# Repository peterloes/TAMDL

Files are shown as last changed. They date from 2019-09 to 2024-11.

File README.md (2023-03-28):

# Timed Animal Manipulation Data Logger (TAMDL)
### use timers to trigger your devices

Authors: Loës P., Kempenaers B. (2019) 

Platform for animal observation and manipulation. 

An efficient system to monitor animal behaviour in wildlife
as well as in laboratory settings.

-	Compatible with different RFID systems and triggers
-	Low power consumption and specific data collection lead to long lasting collection periods
-	Applicable world-wide due to its compatibility with different types of radio clock receivers 
-	High observation quality through low disturbance of the animals
- Three user-defined power outputs that can individually be switched on or off at user-defined times

My image

- Time Synchronization with atomic clock once a day to ensure optimal data quality
- Current Control twice a day
- Forecast for Battery-Change implemented
- Energy Bypass so that Date and Time are maintained even when changing battery
- Hyperterminal Output, to get real-time data to the computer/laptop
- Low-Power Device 
- Measure Voltage and Current from your triggered devices 
 
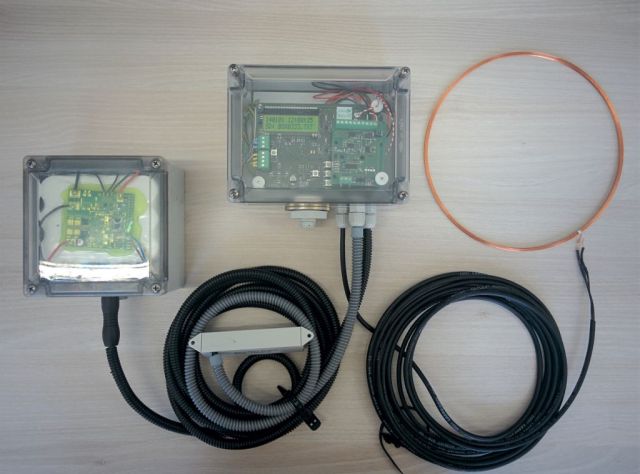
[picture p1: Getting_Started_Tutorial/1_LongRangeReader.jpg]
My image


Picture: Prototype "Activity Logger" with RFID-Reader

https://github.com/peterloes/TAMDL/blob/master/Getting_Started_Tutorial/1_poster_overview_2.pdf

Timed camera trap on nestbox top:

https://github.com/peterloes/TAMDL/blob/master/Getting_Started_Tutorial/1_poster_overview_1.pdf

Raw data on SD Card:

https://github.com/peterloes/TAMDL/blob/master/Getting_Started_Tutorial/6_rawdata_BOX0999.TXT

Configuration data on SD Card:

https://github.com/peterloes/TAMDL/blob/master/Software/CONFIG.TXT

Optional components:

https://github.com/peterloes/Light_Barrier

https://github.com/peterloes/Servo_Engine

https://github.com/peterloes/Linear_Engine

https://github.com/peterloes/Booter_RFID-MS_MOMO_TAMDL

https://github.com/peterloes/Clock_receiver_RFID-MS_MOMO_TAMDL

Manufacture:

https://github.com/peterloes/TAMDL/blob/master/Getting_Started_Tutorial/5_Supplier.txt

C is the Greenest Programming Language

To achieve its power and energy-efficiency features, EFM32 products utilize ultralow active and idle power,
fast wakeup and processing times, and most important, the ability to intelligently interact with peripherals
and sensors autonomously without waking up the CPU and consuming more power.

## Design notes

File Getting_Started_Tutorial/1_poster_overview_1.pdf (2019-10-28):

### Timed Animal Manipulation Data Logger (TAMDL)

### Automating the recording and manipulation of animal behavior

Peter Loës & Peter Skripsky Department Kempenærs

Uses of TAMDL:

- Timed activation of devices such as solar panels, automatic feeders, animal traps, and other electronic devices
- Ideal for nest boxes, roosting boxes, and open nests
- Can be combined with many external triggers such as pit tag (RFID) readers, camera traps, light barriers, lights, etc.
- Manipulation of organisms at e.g. simulating early light/dawn with timed lights in nest boxes

8,3 mm

RFID tag/transponder

Timed camera
trap on top

Timed RFID
reader in nest
box (records ID)

Example use of TAMDL (e.g. nest box):

Benefits of TAMDL:

- Automated device → no observer bias, accurate recording, minimal disturbance to study species
- Only uses sleep and deep sleep mode to save battery life
- Large SD card data storage
- Timer connected to external devices (e.g. camera trap) lets you control the amount of data collected and energy output

LCD can be used to view
settings (pushbuttons on
the circuit board to go
through different settings)

Example Timer Setup:

Operating times for UA1 output [hour:min] → Camera Trap
UA1_ON_TIME_1 | = 23:00
UA1_OFF_TIME_1 | = 00:00
UA1_ON_TIME_2 | = 05:00
UA1_OFF_TIME_2 | = 06:00
UA1_ON_TIME_3 | = 11:00
UA1_OFF_TIME_3 | = 12:00
UA1_ON_TIME_4 | = 17:00
UA1_OFF_TIME_4 | = 18:00
Operating times for UA2 output [hour:min] → RFID Reader
UA2_ON_TIME_1 | = 09:00
UA2_OFF_TIME_1 | = 11:00

Max-Planck-Institut
für Ornithologie

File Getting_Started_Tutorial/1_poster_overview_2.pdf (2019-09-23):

### Timed Animal Manipulation Data Logger (TAMDL)

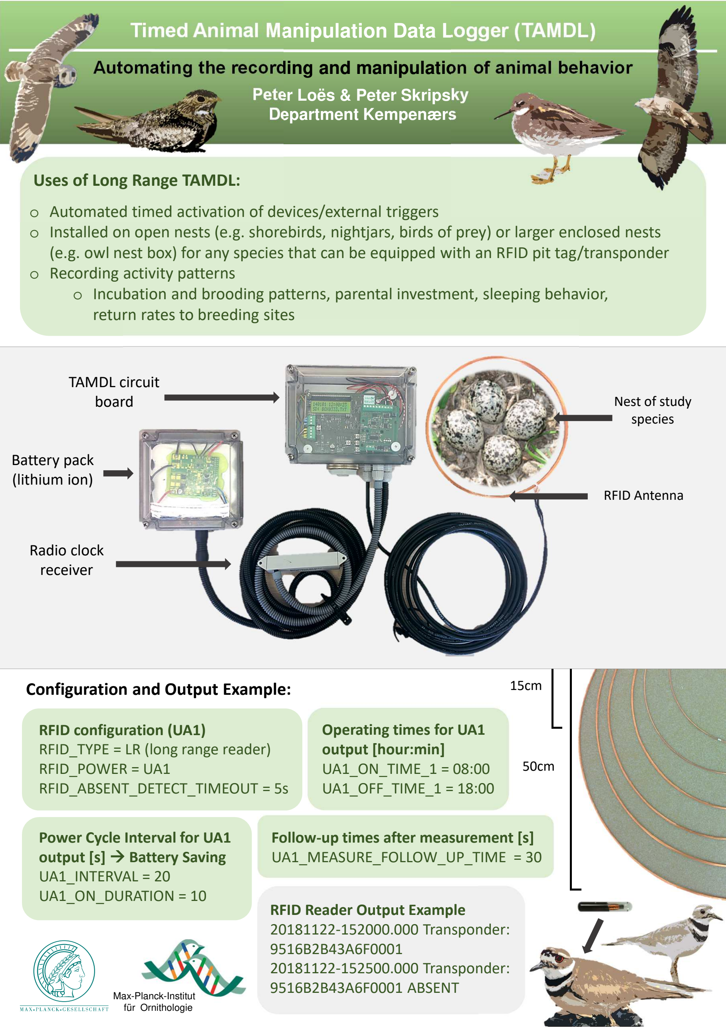
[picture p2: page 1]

Automating the recording and manipulation of animal behavior

Peter Loës & Peter Skripsky Department Kempenærs

TAMDL circuit
board

Battery pack
(lithium ion)

Radio clock
receiver

RFID Antenna

Nest of study
species

Uses of Long Range TAMDL:

- Automated timed activation of devices/external triggers
- Installed on open nests (e.g. shorebirds, nightjars, birds of prey) or larger enclosed nests (e.g. owl nest box) for any species that can be equipped with an RFID pit tag/transponder
- Recording activity patterns
- Incubation and brooding patterns, parental investment, sleeping behavior,
return rates to breeding sites

Configuration and Output Example:

50cm

15cm

Operating times for UA1
output [hour:min]
UA1_ON_TIME_1 = 08:00
UA1_OFF_TIME_1 = 18:00

Power Cycle Interval for UA1 output [s] → Battery Saving UA1_INTERVAL = 20
UA1_ON_DURATION = 10

RFID configuration (UA1)
RFID_TYPE = LR (long range reader) RFID_POWER = UA1
RFID_ABSENT_DETECT_TIMEOUT = 5s

RFID Reader Output Example 20181122-152000.000 Transponder: 9516B2B43A6F0001
20181122-152500.000 Transponder: 9516B2B43A6F0001 ABSENT Max-Planck-Institut

für Ornithologie

Follow-up times after measurement [s] UA1_MEASURE_FOLLOW_UP_TIME = 30

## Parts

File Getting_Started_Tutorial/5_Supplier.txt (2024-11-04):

Active antennas
DCF77 Empfänger AASV DCFn PON/Ri/1m Aktivantenne SV DCFn 

HKW-Elektronik GmbH
Jörg Schneider

Eisenacher Str. 42 b
99848 Wutha-Farnroda / Thür.
Germany
Phone:  +49 (0)36921 3080 130
mailto:    schneider@hkw-elektronik.de
www.hkw-elektronik.de

Lithium Ionen rechargeable battery pack Art.Nr. 60.16294 Panasonic NCR 18650GA 4S2P
14,4Volt 6900mAh inklusive SMBus Kabel je. 150mm 

DYNAMIS Batterien GmbH
Josef Pfeil

Brühlstraße 15  D- 78465 Dettingen / Konstanz
Tel. +49 (0) 75 33/93 669-15
mailto:josef.pfeil@dynamis-batterien.de
www.dynamis-batterien.de

RFID Reader Lichtschranke Artikenr.:170201-00/0 (Long Range)
//Input power supply max. 15Volt

AFRO Fluginstrumente GmbH
Andreas Frommwieser

Bahnhofstr. 37
D - 83253 Rimsting / Chiemsee
Tel.: +49 (0)8051 / 61249
Mobil:+49 (0)151/22 684 697
www.AFRO-Fluginstrumente.de
A.Frommwieser@AFRO-Fluginstrumente.de

MOUSER ELECTRONICS

Texas Instruments 12-mm low-frequency (LF) glass transponders
Frequency of 134.2 kHz
Artikelnr.: 595-TRPGR30ATGC

Supplier of all Electronic Boards

Top-Print Electronic GmbH
Oskar Schmid

Rosenheimer Landstr. 129a
85521 Ottobrunn
Germany
Tel.: +49-89-60668047
Fax: +49-89-60668049
mailto: info@top-print.eu
https://www.leiterplatten-muenchen.de/

RFID reader
Nanomodule Multi 125LV A/1.11 (T3NM-LV) 125kHz +/-0,5% Art.Nr. ART10413
ANT002 Rundspule 47mm, 490µH Art.Nr. ART 10668

Elatec GmbH
Felix Ellspermann

Zeppelinstr. 1
82178 Puchheim 
Germany
Tel: +49 89 552 9961 120
mailto: f.ellspermann@elatec.com
www.elatec-rfid.com

Small sized transponder, not uniqued.
GlassTag 1,41x8,3mm EM4305 134kHz

Programming required for transponders.

Rasmus Forntheil
Product Manager Animal ID
RBIS Europe, Smartrac Specialty GmbH

e: rasmus.forntheil@eu.averydennison.com
t: +49 (0) 2265 9919-14  |  m: +49 (0) 173 5688184
Gewerbeparkstr. 10, 51580 Reichshof-Wehnrath, Germany

Internet: https://www.averydennison.com/en/home.html

Protective coating with Schmelzharz Bectron MR3404

KC – Kunststoff- Chemische Produkte GmbH
Holger Sarau-Burghardt

Leonberger Straße 86 
DE 71292 Friolzheim
phone: +49 (0)7044 9425 13
e-mail: h.sarau-burghardt@kc-produkte.com
http: www.conformalcoating.de

Industrial SD Cards ATP 2GB
https://www.atpinc.com/products/industrial-sd-cards

FTDI Chip cable (3.5mm Audio Jack to USB)
TTL-232R-3V3-AJ

Housing
https://www.spelsberg.de/industrieleergehaeuse/glatt-mit-befestigungsnocken/20100701/
TG PC 1612-9-to
Artikelnummer: 20100701 | Maße: 162 x 122 x 90 mm
Leergehäuse IP66 / IP67 Polycarbonat

iTracker DashCam Mini0801
Please contact me to get the electronic board for IR_Light_DashCam. (Hardware_EagleFiles)

Docklight RS232 Terminal / RS232 Monitor
https://docklight.de/information/

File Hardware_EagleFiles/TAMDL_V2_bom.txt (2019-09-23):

Part  Value                                             Device                  Package                Description                                                    MPN     OC_FARNELL OC_NEWARK PACKAGE  SUPPLIER         
C1    100µF/25V                                         CPOL-EUE                PANASONIC_E            POLARIZED CAPACITOR, European symbol                                                                                  
C2    10µF/25V                                          C-EUC1206               C1206                  CAPACITOR, European symbol                                                                                            
C3    22µF/10V                                          C-EUC0603               C0603                  CAPACITOR, European symbol                                                                                            
C4    EECS0HD 224;Panasonic                             GOLDCAPSPK-V            GOLDCAPSPK-V                                                                                                                                 
C5    100µF/25V                                         CPOL-EUE                PANASONIC_E            POLARIZED CAPACITOR, European symbol                                                                                  
C6    100µF/25V                                         CPOL-EUE                PANASONIC_E            POLARIZED CAPACITOR, European symbol                                                                                  
C7    100nF/16V                                         C-EUC0805               C0805                  CAPACITOR, European symbol                                                                                            
C8    100nF/16V                                         C-EUC0805               C0805                  CAPACITOR, European symbol                                                                                            
C9    10µ/25V                                           C-EUC1206               C1206                  CAPACITOR, European symbol                                                                                            
C10   100n                                              C_SMD0805               0805                                                                                                                                         
C11   1u                                                C_SMD0805               0805                                                                                                                                         
C12   18p                                               C_SMD0805               0805                                                                                                                                         
C13   12p                                               C_SMD0805               0805                                                                                                                                         
C14   100n                                              C_SMD0805               0805                                                                                                                                         
C15   100n                                              C_SMD0805               0805                                                                                                                                         
C16   100n                                              C_SMD0805               0805                                                                                                                                         
C17   18p                                               C_SMD0805               0805                                                                                                                                         
C18   12p                                               C_SMD0805               0805                                                                                                                                         
C19   10µ                                               C_SMD0805               0805                                                                                                                                         
C20   100n                                              C_SMD0805               0805                                                                                                                                         
C21   100n                                              C_SMD0805               0805                                                                                                                                         
C22   100n                                              C_SMD0805               0805                                                                                                                                         
C23   100n                                              C_SMD0805               0805                                                                                                                                         
C24   100n                                              C_SMD0805               0805                                                                                                                                         
C25   10µ                                               C_SMD0805               0805                                                                                                                                         
C26   10nF                                              C-EUC0603               C0603                  CAPACITOR, European symbol                                                                                            
C27   10nF                                              C-EUC0603               C0603                  CAPACITOR, European symbol                                                                                            
C28   10nF                                              C-EUC0603               C0603                  CAPACITOR, European symbol                                                                                            
C29   10nF                                              C-EUC0603               C0603                  CAPACITOR, European symbol                                                                                            
C30   10nF                                              C-EUC0603               C0603                  CAPACITOR, European symbol                                                                                            
C31   10n                                               C-EUC0603               C0603                  CAPACITOR, European symbol                                                                                            
C32   100nF                                             C-EUC0603               C0603                  CAPACITOR, European symbol                                                                                            
C33   100nF                                             C-EUC0603               C0603                  CAPACITOR, European symbol                                                                                            
C34   4.7µF                                             C-EUC1210               C1210                  CAPACITOR, European symbol                                                                                            
C35   4.7µF                                             C-EUC1210               C1210                  CAPACITOR, European symbol                                                                                            
C36   n.b.                                              C-EUC1210               C1210                  CAPACITOR, European symbol                                                                                            
C37   n.b.                                              C-EUC1210               C1210                  CAPACITOR, European symbol                                                                                            
C38   10nF                                              C-EUC0603               C0603                  CAPACITOR, European symbol                                                                                            
C39   10nF                                              C-EUC0603               C0603                  CAPACITOR, European symbol                                                                                            
C40   100nF                                             C-EUC0603               C0603                  CAPACITOR, European symbol                                                                                            
C41   100nF                                             C-EUC0603               C0603                  CAPACITOR, European symbol                                                                                            
C42    n.b.                                             C-EUC0603               C0603                  CAPACITOR, European symbol                                                                                            
C43    n.b.                                             C-EUC0603               C0603                  CAPACITOR, European symbol                                                                                            
C44   4.3nF                                             C-EUC0603               C0603                  CAPACITOR, European symbol                                                                                            
C45   4.3nF                                             C-EUC0603               C0603                  CAPACITOR, European symbol                                                                                            
C46   24pF                                              C-EUC0603               C0603                  CAPACITOR, European symbol                                                                                            
C47   24pF                                              C-EUC0603               C0603                  CAPACITOR, European symbol                                                                                            
C48    n.b.                                             C-EUC0603               C0603                  CAPACITOR, European symbol                                                                                            
C49    n.b                                              C-EUC0603               C0603                  CAPACITOR, European symbol                                                                                            
C50   22µF                                              C-EUC1210               C1210                  CAPACITOR, European symbol                                                                                            
C51   22µF                                              C-EUC1210               C1210                  CAPACITOR, European symbol                                                                                            
C52   22µF                                              C-EUC1210               C1210                  CAPACITOR, European symbol                                                                                            
C53   22µF                                              C-EUC1210               C1210                  CAPACITOR, European symbol                                                                                            
C54   n.b.                                              C-EUC1210               C1210                  CAPACITOR, European symbol                                                                                            
C55   n.b.                                              C-EUC1210               C1210                  CAPACITOR, European symbol                                                                                            
C56   10µF                                              C-EUC1206               C1206                  CAPACITOR, European symbol                                                                                            
C57   10µF                                              C-EUC1206               C1206                  CAPACITOR, European symbol                                                                                            
C58   100nF                                             C-EUC0603               C0603                  CAPACITOR, European symbol                                                                                            
C59   100nF                                             C-EUC0603               C0603                  CAPACITOR, European symbol                                                                                            
C60   100nF                                             C-EUC0603               C0603                  CAPACITOR, European symbol                                                                                            
C61   1nF                                               C-EUC0603               C0603                  CAPACITOR, European symbol                                                                                            
C62   1nF                                               C-EUC0603               C0603                  CAPACITOR, European symbol                                                                                            
C63   100nF                                             C-EUC0603               C0603                  CAPACITOR, European symbol                                                                                            
C64   470n                                              C-EUC0805               C0805                  CAPACITOR, European symbol                                                                                            
C65   100n                                              C-EUC1206               C1206                  CAPACITOR, European symbol                                                                                            
D1    BAT54C                                            D2A_SOT23               SOT-23$1               Dual DIODE                                                                                                            
D2    BAT54C                                            D2A_SOT23               SOT-23$1               Dual DIODE                                                                                                            
D3    BAT54C                                            D2A_SOT23               SOT-23$1               Dual DIODE                                                                                                            
D4    B360B                                             SCHOTTKY-DIODESMD       SMB                    Schottky Diode                                                                                                        
D5    B360B                                             SCHOTTKY-DIODESMD       SMB                    Schottky Diode                                                                                                        
D6    MBR2H200SFT1G                                     SMF5.0AT1               SOD123FL               200 W Transient Voltage Suppressor                                                                                    
D7    MBR2H200SFT1G                                     SMF5.0AT1               SOD123FL               200 W Transient Voltage Suppressor                                                                                    
F1    MF-USMF110                                        PFUF                    PFUF_1210POLY                                                                                                                                
F2    MF-USMF110                                        PFUF                    PFUF_1210POLY                                                                                                                                
F3    MF-USMF110                                        PFUF                    PFUF_1210POLY                                                                                                                                
F4    MF-USMF150                                        PFUF                    PFUF_1210POLY                                                                                                                                
F5    MF-USMF150                                        PFUF                    PFUF_1210POLY                                                                                                                                
IC1   TPS62125                                          TPS62125                DSG_PWSO-N8_EXP                                                                                                                              
IC2   EFM32G230F128                                     EFM32G230F128           QFN64                  EFM32G230F128 Gecko Microcontroller in 9mm x 9mm QFN64 package                                                        
IC3   TPS54240DGQR                                      TPS54240DGQR            S-PDSO-G10                                                                                                                                   
IC4   TPS54240DGQR                                      TPS54240DGQR            S-PDSO-G10                                                                                                                                   
IC5   LTC6102IDD-1                                      LTC6102IDD-1            DFN8-LEAD                                                                                                                                    
IC6   LTC6102IDD-1                                      LTC6102IDD-1            DFN8-LEAD                                                                                                                                    
J1    LUMBERG1502_01                                    LUMBERG1502_01          LUMBERG1502_01                                                                                                                               
L1    LPS3008/22µH                                      LPS3008                 LPS3008                                                                                                                                      
L2    BLM21B102S                                        WE-CBF-7427920_0805     0805                   SMD EMI Suppression Ferrite Beads WE-CBF                       7427920 1635707    08P2358   IND-0805 Wuerth Elektronik
L3    PIS4728                                           DR127                   DR127                  High Power Density, High Efficiency, Shielded Inductors                                                               
L4    PIS4728                                           DR127                   DR127                  High Power Density, High Efficiency, Shielded Inductors                                                               
LCD1  Buchsenleisten(Conrad 741360) (n.b.)EA_DOGM162L_A EA_DOGM162              EA_DOGM                ELECTRONIC ASSEMBYL GmbH                                                                                              
LED1  SML-H12U8TT86                                     LEDCHIPLED_0805         CHIPLED_0805           LED                                                                                                                   
LED2  SML-H12Y8TT86                                     LEDCHIPLED_0805         CHIPLED_0805           LED                                                                                                                   
LED3  SML-H12Y8TT86                                     LEDCHIPLED_0805         CHIPLED_0805           LED                                                                                                                   
LED4  SML-H12Y8TT86                                     LEDCHIPLED_0805         CHIPLED_0805           LED                                                                                                                   
LED5  SML-H12Y8TT86                                     LEDCHIPLED_0805         CHIPLED_0805           LED                                                                                                                   
LED6  SML-H12Y8TT86                                     LEDCHIPLED_0805         CHIPLED_0805           LED                                                                                                                   
LED7  SML-H12U8TT86                                     LEDCHIPLED_0805         CHIPLED_0805           LED                                                                                                                   
LED8  (n.b.)                                            LEDCHIPLED_0805         CHIPLED_0805           LED                                                                                                                   
LED9  (n.b.)                                            LEDCHIPLED_0805         CHIPLED_0805           LED                                                                                                                   
LSP1  (n.b.)SE13                                        SE13                    SE13                   SOLDER PAD E1542,  drill 1,3mm, distributor Buerklin, 07F815                                                          
LSP2  (n.b.)SE13                                        SE13                    SE13                   SOLDER PAD E1542,  drill 1,3mm, distributor Buerklin, 07F815                                                          
PAD1  (n.b.)                                            SMD2                    SMD1,27-2,54           SMD PAD                                                                                                               
PASS1 ROUND_1MM1.5                                      ROUND_1MM1.5            ROUND2_1.5MM                                                                                                                                 
PASS2 ROUND_1MM1.5                                      ROUND_1MM1.5            ROUND2_1.5MM                                                                                                                                 
PASS3 ROUND_1MM1.5                                      ROUND_1MM1.5            ROUND2_1.5MM                                                                                                                                 
PASS4 ROUND_1MM1.5                                      ROUND_1MM1.5            ROUND2_1.5MM                                                                                                                                 
Q1    SI7121DN                                          TRANSISTOR-FET_SI7113DN TRANSISTOR-FET_1212-8S                                                                                                                       
Q2    CM7V, 32768Hz/12.5pF                              CRYSTAL2P               CRYSTAL2P3.2X1.5       Quarz Crystal                                                                                                         
Q3    NX5032GA/32MHz/8pF                                CRYSTAL2P5.0X3.2        CRYSTAL2P5.0X3.2       Quarz Crystal                                                                                                         
R1    1K2                                               R-EU_R0805              R0805                  RESISTOR, European symbol                                                                                             
R2    1k                                                R-EU_R0805              R0805                  RESISTOR, European symbol                                                                                             
R3    1k                                                R-EU_R0805              R0805                  RESISTOR, European symbol                                                                                             
R4    1K2                                               R-EU_R0805              R0805                  RESISTOR, European symbol                                                                                             
R5    100k                                              R-EU_R0805              R0805                  RESISTOR, European symbol                                                                                             
R6    100K                                              R-EU_R0805              R0805                  RESISTOR, European symbol                                                                                             
R7    1M47                                              R-EU_R0805              R0805                  RESISTOR, European symbol                                                                                             
R8    200K                                              R-EU_R0805              R0805                  RESISTOR, European symbol                                                                                             
R9    30K9                                              R-EU_R0805              R0805                  RESISTOR, European symbol                                                                                             
R10   100K                                              R-EU_R0805              R0805                  RESISTOR, European symbol                                                                                             
R11   2M                                                R-EU_R0805              R0805                  RESISTOR, European symbol                                                                                             
R12   560K                                              R-EU_R0805              R0805                  RESISTOR, European symbol                                                                                             
R13   100                                               R-EU_R0805              R0805                  RESISTOR, European symbol                                                                                             
R14   1                                                 R-EU_R0805              R0805                  RESISTOR, European symbol                                                                                             
R15   1K                                                R-EU_R0805              R0805                  RESISTOR, European symbol                                                                                             
R16   1K                                                R-EU_R0805              R0805                  RESISTOR, European symbol                                                                                             
R17   1K                                                R-EU_R0805              R0805                  RESISTOR, European symbol                                                                                             
R18   1K                                                R-EU_R0805              R0805                  RESISTOR, European symbol                                                                                             
R19   1K                                                R-EU_R0805              R0805                  RESISTOR, European symbol                                                                                             
R20   100K                                              R-EU_R0805              R0805                  RESISTOR, European symbol                                                                                             
R21   100K                                              R-EU_R0805              R0805                  RESISTOR, European symbol                                                                                             
R22   100K                                              R-EU_R0805              R0805                  RESISTOR, European symbol                                                                                             
R23   100K                                              R-EU_R0805              R0805                  RESISTOR, European symbol                                                                                             
R24   100K                                              R-EU_R0805              R0805                  RESISTOR, European symbol                                                                                             
R25   10K                                               R-EU_R0805              R0805                  RESISTOR, European symbol                                                                                             
R26   10K                                               R-EU_R0805              R0805                  RESISTOR, European symbol
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

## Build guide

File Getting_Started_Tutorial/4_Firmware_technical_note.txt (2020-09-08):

Timed Animal Manipulation Data Logger (TAMDL).

Version 1.4
- Added support for battery controller TI bq40z50.
  LogBatteryInfo: Removed SBS_ManufacturerData.
  Display SBS_RunTimeToEmpty in days/hours/min.
  Display SBS_SerialNumber as hex value.
- CheckAlarmTimes to call the respective alarm action if the current time matches the alarm time.
  Reading the configuration file CONFIG.TXT from the SD-Card and set-up alarm action.
- Corrected decoding of Short-Range(SR) RFID Reader transponder ID.

It consists of the following components:
- Control.c - Sequence Control module.
- CfgData.c - Handling of configuration data.
- ExtInt.c - External interrupt handler.
- Keys.c - Key interrupt handling and translation.
- AlarmClock.c - Alarm clock and timers facility.
- DCF77.c - DCF77 Atomic Clock Decoder
- clock.c - An implementation of the POSIX time() function.
- LCD_DOGM162.c - Driver for the DOGM162 LC-Display.
- DisplayMenu.c - Display manager for Menus and LCD.
- DM_Clock_Transp.c - Display Module to show Clock and Transponder number
- DM_PowerOutput.c - Display Module to switch @ref Power_Outputs
- DM_BatteryStatus.c - Display Module to show current Battery Status
- DM_PowerTimes.c - Display Module to show all configured ON/OFF Times.
- RFID.c - RFID reader to receive transponder IDs.
- BatteryMon.c - Battery monitor, periodically reads the state of the
  battery via the SMBus.
- LEUART.c - The Low-Energy UART can be used as monitoring and debugging
  connection to a host computer.
- microsd.c - Together with the files "diskio.c" and "ff.c", this module
  provides an implementation of a FAT file system on the @ref SD_Card.
- Logging.c - Logging facility to send messages to the LEUART and store
  them into a file on the SD-Card.
- eeprom_emulation.c - Routines to store data in Flash, taken from AN0019.
- PowerFail.c - Handler to switch off all loads in case of Power Fail

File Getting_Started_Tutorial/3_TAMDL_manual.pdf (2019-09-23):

## Max Planck Institute for Ornithology

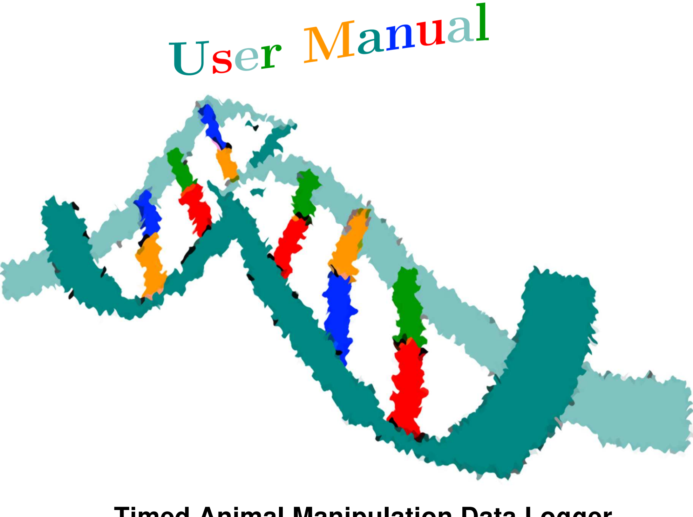
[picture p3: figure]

11.02.2019 | https://www.orn.mpg.de | Copyright 2019 ©, MPIO Seewiesen | page 1

# Timed Animal Manipulation Data Logger (TAMDL)

Created by Peter Loës
11.02.2019

In order of the Max Planck Institute for Ornithology at Seewiesen (Germany)

Disclaimer and Copyright

11.02.2019 | https://www.orn.mpg.de | Copyright 2019 ©, MPIO Seewiesen | page 2

## Disclaimer

The Timed Animal Manipulation Data Logger (TAMDL) is to be used only as that described in this document. Any other method of usage is not permitted. If damage occurs due to incorrect usage, the manufacturer of the Timed Animal Manipulation Data Logger (TAMDL) is not liable.

## Copyright ©

The Copyright for this user manual remains with the manufacturer. Text and figures meet the latest technical status at the time of publication. Subject to change. The content of the user manual shall not affect any claims of the purchaser. The editor also welcomes suggestions of any possible improvements you may have or whether any errors are encountered.

List of abbrevations

11.02.2019 | https://www.orn.mpg.de | Copyright 2019 ©, MPIO Seewiesen | page 3

## Table of contents

List of abbreviations | 7
System Overview | 8
General Description of Functions | 8
System configuration main circuit board | 10
Hardware Illustration (TAMDL) | 10
Debug Interface (DBG) | 13
Liquid Crystal Display (LCD) | 13
EFM32 Microcontroller | 13
Current Sense Amplifier (U1 and U2) | 15
Battery in- and output | 15
UA1 and UA2 out | 15
Connections for buses of devices | 15
Connections for the SMBus of the battery pack | 16
Connecting terminal for the radio clock | 16
Reset pushbutton | 16
LEDs | 17
Pushbuttons | 17
Gold cap capacitor | 17
Power supply TAMDL | 18
Jack connector as interface to a PC | 18

List of abbrevations

11.02.2019 | https://www.orn.mpg.de | Copyright 2019 ©, MPIO Seewiesen | page 4
Output voltages (Down converter) | 19
SD Memory Card Connector | 19
Hardware illustration radio clock receiver | 19
Radio clock | 20
Smart Recorder (Hardware) | 21
Hardware illustration | 21
RFID reader for transponders | 22
Dashcam | 25
Accumulator | 26
Housing | 27
Housing for the main board | 27
Housing for the accumulator | 28
General working conditions | 29
Energy supply | 30
Current supply | 31
ARM Cortex Processor | 31
RFID | 31
Radio clock | 31
LED | 31
Accumulator LEDs and self-discharge | 32
Overview of the nominal currents | 32
Overview of the currents in the different operating modes | 33

List of abbrevations

11.02.2019 | https://www.orn.mpg.de | Copyright 2019 ©, MPIO Seewiesen | page 5
Voltage supply | 34
Electrical energy storage | 35
Accumulator | 35
Capacitor | 35
Conversion losses | 36
Range estimation of the accumulator | 36
Operation of the Smart Recorder | 37
Accumulator replacement | 41
Reasons for accumulator replacement | 41
Placement of the accumulator | 42
SD card change | 42
Software update | 43
Loading the accumulator | 43
Recharger | 43
Charging method IUoU | 44
Charge time | 45
Troubleshooting Smart Feeder | 45
Troubleshooting in the field | 46
Troubleshooting in the laboratory | 46
Software | 47
Reset | 47
Possibilities to perform a manual reset | 47

List of abbrevations

11.02.2019 | https://www.orn.mpg.de | Copyright 2019 ©, MPIO Seewiesen | page 6
Procedure after reset | 47
Reset protocol | 48
Data storage | 49
Periodic routine queries | 54
Time update | 54
Battery status query | 54
Recorded events | 55
Light barrier activity | Fehler! Textmarke nicht definiert.
Transponder activity | 55
Servomotor activity | Fehler! Textmarke nicht definiert.
Connections for possible recording devices (camera) | Fehler!
Textmarke nicht definiert.
Standard recording | 56
Power Good and Power Fail | 57
Occurrences when it is not possible to write on the SD card | 58
Procedure after button usage | 59
Update options | 59
IAR Systems Debug Probe | 59
With USB on 10-pole Debug Interface Connector | 60
Via SD card and boot loader | 60
Contact details | 61

### 8. Links to the datasheets | 62

List of abbrevations

11.02.2019 | https://www.orn.mpg.de | Copyright 2019 ©, MPIO Seewiesen | page 7

## List of abbreviations

RFID | radio-frequency identification
EFM | Energy Friendly Microcontroller
PCB | printed circuit board
DCF | D for Deutschland (Germany), C for long-wave transmitter, F due to the vicinity to the Town Frankfurt
ARM | Advanced RISC Machines
SD CARD | Secure Digital Memory Card
PIT | Passive Integrated Transponder
LEUART | Low Energy Universal Asynchronous Receiver/Transmitter
USB | Universal Serial Bus
TAMDL | Timed Animal Manipulation Data Logger

Content

11.02.2019 | https://www.orn.mpg.de | Copyright 2019 ©, MPIO Seewiesen | page 8

## System Overview

## General Description of Functions

The Timed Animal Manipulation Data Logger (TAMDL) has mainly been developed to simplify the recording and manipulation of animal behaviour and to collect data, e.g. of weight by timing the activation and inactivation of several devices, for example, dashcams and scales. Up to three devices can be connected to TAMDL simultaneously.

One other possible device that could be activated by TAMDL is an RFID reader. That device can read out transponders in case an animal is equipped with one and thereby identify the individual. This technology can be used for every animal species on, or in which it is possible to attach a RFID transponder of the size of a rice grain. Within a population of several individuals carrying a RFID transponder, the Timed Animal Manipulation Data Logger can switch on the reading device to certain times, e.g. around sunset, to identity the animals sleeping in a nest box. Whenever an individual with transponder e.g. enters, its transponder code and the timestamp are saved on a SD-card. A thinkable combination of that function with other devices might be a scale. TAMDL could thereby not only record the individual sleeping inside the nest box, but also take its weight. Via the timer, another period to scale the individual could be set around dawn to eventually compare its weight before and after sleep. Furthermore, the bird’s behaviour could be manipulated by switching on some light inside a nest box at a certain time before the actual sunrise to artificially elongate daytime. TAMDL could simultaneously switch on a camera to record the bird’s reaction during that period of time and switch the camera off after some minutes. The control of the camera could also be related to a certain transponder code. This would enable researchers to only record the behaviour of certain birds and thereby efficiently decrease working time by providing much less video material to go through.

To achieve a flexible operation in the field, the Timed Animal Manipulation Data Logger is supplied with electrical energy by a rechargeable accumulator. The huge advantage of TAMDL is that it can activate connected devices for a pre-set time and thereby save a lot of energy. These periods of time can also be in the middle of the night – sparing biologists nightshifts.

11.02.2019 | https://www.orn.mpg.de | Copyright 2019 ©, MPIO Seewiesen | page 9

The use of electronic devices in the field and nature requires special features in order to operate correctly. Special developments are needed in order to cope with changes in ambient temperature, humidity, pressure and when the electrical power grid is unavailable. However, such developments can be time-consuming and costintensive. Much iteration in the development is required in order to ensure a stable functioning of electronic products in the wild. A key strength of the Timed Animal Manipulation Data Logger is that it runs autonomously. During the development, special attention was paid to developing an energy saving operation, so that a battery pack would only have to be changed every two weeks up to several months, depending on the activity of the connected devices. The SD cards used have enough memory space to save data for several months of data collection. These low operating expenses make the Timed Animal Manipulation Data Logger (TAMDL) ideal for a use in isolated locations without grid connection. Also, TAMDL can be placed wherever needed. A special housing provides protection against any weather conditions.

Finally, biological data is optimally collected when disturbance to the animal’s behaviour due to human presence is minimised. Compared with observations or manual handling, data generation is less error-prone and an increase of data volume is easily realizable. TAMDL also supports an activation and deactivation of video devices or cameras.

Thinking outside an ornithological context, the Timed Animal Manipulation Data Logger is very multifunctional. As it is developed to work outside and to time the functions of devices, it could be used in several outdoor/energy saving contexts.

Some examples of potential uses are:

- control and manipulation of energy consumption (e.g. cooling boxes,

dishwashers, etc.)
- timed activation/inactivation of sillcocks
- actuating trap releaser (e.g. 3x a day right before arrival of experimenter)
- targeted power-up, for example, of solar panels (only when sun is highest)
- control of flaps and automatic feeders (e.g. for cattle, zoo animals, pets, etc.)
- outdoor/energy solutions for up to 3 consumers
- manipulation and data collection of certain individuals in e.g. nest or roosting

boxes (e.g. bats, birds)

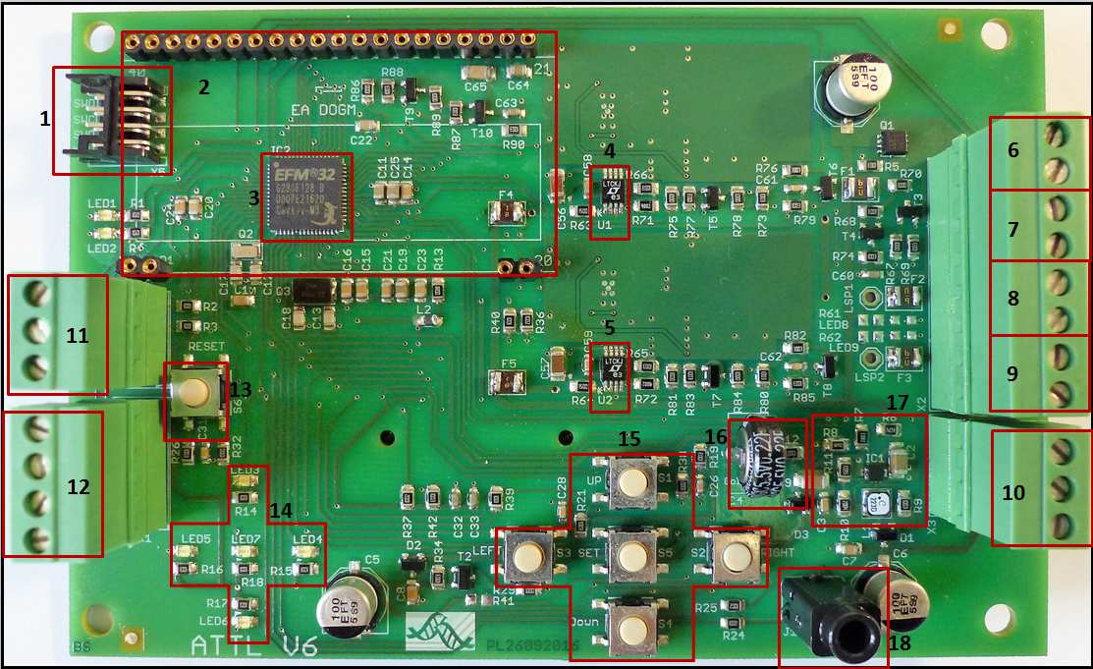
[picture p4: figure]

11.02.2019 | https://www.orn.mpg.de | Copyright 2019 ©, MPIO Seewiesen | page 10

## System configuration main circuit board

The smart feeder was developed over several years. After five years of development a reliable and efficient version was completed, which is described comprehensively in this manual. Additional detailed information, particularly concerning the electronic configuration, can be found in the datasheet.

Hardware Illustration (TAMDL)

Front side

Back side

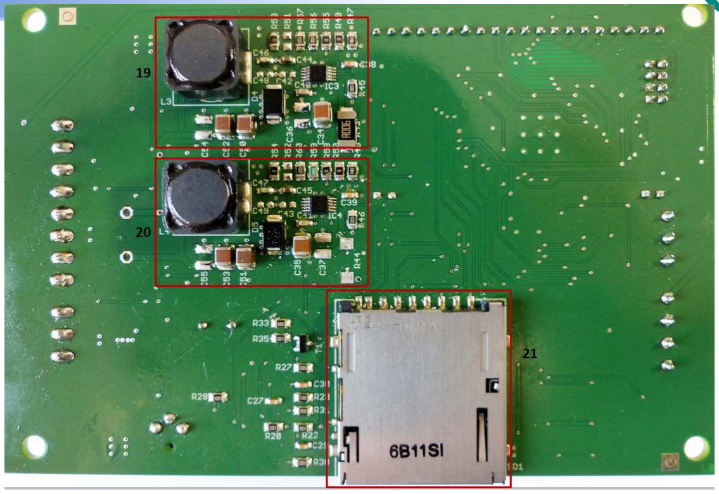
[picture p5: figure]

11.02.2019 | https://www.orn.mpg.de | Copyright 2019 ©, MPIO Seewiesen | page 11

11.02.2019 | https://www.orn.mpg.de | Copyright 2019 ©, MPIO Seewiesen | page 12

1 Debug Interface

2 LC Display

3 Microcontroller EFM32G230

4 Current Sense Amplifier U1

5 Current Sense Amplifier U2

6 Battery input

7 Battery output

8 UA1_OUT

9 UA2_OUT

10 Connections for buses of devices | (e.g. scale, RFID reader, etc.)

11 Connections for the SMBus ‘System Management Bus’ of the battery pack

12 Connecting terminal for radio clock

13 Reset pushbutton

14 LEDs 3 to 7

15 Pushbuttons

16 Gold Cap Capacitor

17 Down converter

18 LEUART connector

19 Output voltage | 3.5V-11V@ 2.5A for e.g. cameras
20 Output voltage | 3.5V-11V@ 2.5A for e.g. cameras

21 SD memory card connector

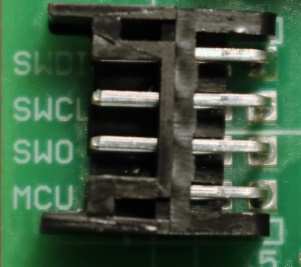
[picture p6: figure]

11.02.2019 | https://www.orn.mpg.de | Copyright 2019 ©, MPIO Seewiesen | page 13

Debug Interface (DBG)

The debug interface software is stored on the microcontroller flash memory. Only after the flash memory contains this information, the hardware can be operated. The connection is either realised directly with a USB cable to the debug interface or with a debugging probe. If the connection is realized directly through the USB cable only HEX files and BIN files can be transferred.

Liquid Crystal Display (LCD)

This kind of display screen utilizes liquid crystals, which influence the polarization direction of light when a certain amount of electrical voltage is applied.

LCD’s consist of segments which can
independently change their transparency.
This is done by a change in the orientation of each segment of the liquid crystals when an electrical voltage is applied. This
then | changes | the | permeability | for
polarized light, which is created by a
backlight.

One can move through the results shown on the LCD via the pushbuttons (see chapter 1.2.13).

EFM32 Microcontroller

So called microcontroller (MCU) are flip chips that, at the same time, contain a processor and peripheral functions. In many MCUs, the internal and program memory are located partially or entirely on the same chip.

EFM32 is a family of microcontrollers offered by Silicon
Laboratories. The EFM32 are 32-bit microcontrollers of different sub-families that use ARM cortex-M3 processors. The energy consumption received special focus during the development, which influenced naming: EFM stands for Energy Friendly

11.02.2019 | https://www.orn.mpg.de | Copyright 2019 ©, MPIO Seewiesen | page 14
Microcontrollers. | The low power demand makes the EFM32 microcontroller
especially suitable for applications with battery supply. EFM32 microcontrollers contain several energy-saving modes that can be changed easily. Additionally, many peripheral devices can be plugged.

Within the Timed Animal Manipulation Data Logger the EFM32G230 microcontroller is used with 128 KB Flash Memory and 16 KB RAM Memory.

The EFM32 series is also known as ‘Gecko’ by the developer, as these animals consume only 10% of the energy used by a mammal of similar size.

Energy Micro states that benchmark measurements with other leading energy saving MCUs found that the EFM32-MCU consumes only a quarter of the energy consumed by the other 8-, 16-, or 32-bit-MCUs.

The EFM32 microcontroller based on the ARM Cortex processor is well suited for energy saving applications such as:

- electricity, gas and water-meters
- factory automation and building automation systems
- alarm and security technology as well as portable applications for medical

engineering or within the fitness sector.

The ARM Cortex-M3 processor is developed by Energy Micro and has been bought by Silicon Labs. Since the used processor works with 32 bit, data processing is much faster than 8 and 16 bit CPUs. Therefore, tasks are completed with less clock cycles, thereby reducing the dwell time in an active mode substantially.

The EFM32G230 contains an UART-interface for communication with external systems, which is especially designed for energy saving. The interface is referred to as LEUART-interface. LEUART is a serial interface, a kind of bus system. Through the LEUART-interface, a jack connector and a USB cable can be used to establish a connection to a computer.

11.02.2019 | https://www.orn.mpg.de | Copyright 2019 ©, MPIO Seewiesen | page 15

Current Sense Amplifier (U1 and U2)

The LTC6102 Current Sense Amplifiers are so called ammeters (from Ampere Meter), that measure the electric current – both from UA1 and UA2. Here, a current shunt measurement is applied. The current gets monitored via the voltage across an external sense resistor (shunt resistor). Internal circuitry converts input voltage to output current, allowing a small sense signal on a large common mode voltage to be translated to a ground-referred signal. Low DC offset allows the use of very low shunt resistor values and large gain-setting resistors. As a result, power loss in the shunt

is reduced. LTC6102IDD-1#PBF Foto

Battery in- and output

The battery output has an output voltage of more than 10 V and can be switched off.

UA1 and UA2 out

UA1 and UA2 create an output voltage of up to 11 V and are secured exits of the two output voltages (chapter 1.2.17).

Connections for buses of devices

Several devices like scales, RFID readers, cameras, etc. can be connected to the TAMDL depending on the aim of the study.

11.02.2019 | https://www.orn.mpg.de | Copyright 2019 ©, MPIO Seewiesen | page 16

Connections for the SMBus of the battery pack

TAMDL supports following standard communication bus systems:

SMBus ‘System Management Bus’ (http://www.smbus.org/) as well as the
I²C ‘Inter-Integrated Circuit Interface’ below a frequency of 100 kHz (https://en.wikipedia.org/wiki/I%C2%B2C).

The System Management Bus (SMBus) is needed for the communication between TAMDL and the microcontroller with ‘Battery management system’ (BMS).
For reading the single registers of the microcontroller with BMS via the SMBus, the software commands ‘SBS Commands’ were installed.

Connecting terminal for the radio clock

Another potential feature of the TAMDL can be a radio clock, which works in a similar way as a normal clock. In periodic intervals a signal to Europe from the long wave antenna in Mainflingen with a frequency of 77.5 MHz is received and synchronized. Long wave signals have
been compared to short waves and medium waves, and have a relatively high range, making it is possible to receive the signal from
Mainflingen with a range of up to 2000 km. On other continents, the time signals can be received as well, though with different frequencies.

Reset pushbutton

A ‘reset’ pushbutton is installed on the mainboard of the Timed Animal Manipulation Data Logger, which restarts TAMDL.

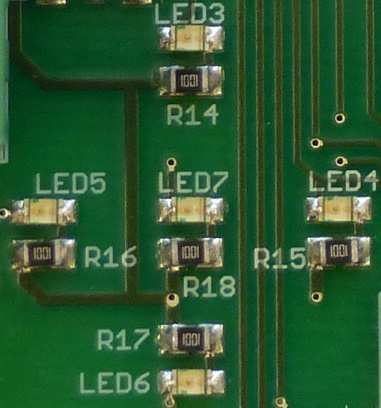
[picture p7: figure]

11.02.2019 | https://www.orn.mpg.de | Copyright 2019 ©, MPIO Seewiesen | page 17

LEDs

The Timed Animal Manipulation Data Logger is equipped with seven LEDs. If the red LED (LED 1) flashes, this indicates that the radio clock is transmitting a signal to the MCU. If the LED 1 blinks longer than 5 minutes or flashes continuously, this indicates
a malfunction. The yellow LED (LED 2) indicates a communication with the SD card. When it flashes, the SD card can be removed or exchanged safely.

LEDs 3 to 7 (yellow) are equivalent to the pushbuttons and accordingly respond to their usage (see next chapter).

Pushbuttons

Besides the reset pushbutton (chapter 1.2.9), there are five pushbuttons installed on the mainboard of the Timed Animal Manipulation Data Logger: Up, Down, Left, Right and Set. They enable navigation through the information shown on the LCD.

Gold cap capacitor

A capacitor (German ‘Kondensator’) is a passive electric component with the ability to store electrical charge and electrical energy of a continuous circuit statically in an electrical field.

When the electrical power supply through the battery is
missing, the capacitor ensures an alternate power supply for the Timed Animal Manipulation Data Logger (TAMDL). The capacitor is charged when the accumulator supplies energy to the system. This allows energy to be obtained for a certain time from the capacitor if it is required.

Especially the clock of the microcontroller continuous to be powered when there is no external electrical power supply.

11.02.2019 | https://www.orn.mpg.de | Copyright 2019 ©, MPIO Seewiesen | page 18

Some applications only become possible through double layered capacitors. Despite its large capacity, it is very small in size. The dielectric strength is not exceptionally high however, with only a few volts. Through its large capacity, the Gold Cap is present to maintain the power supply when the main energy source fails. In devices in which data storage should remain in switched off status, the Gold Cap is particularly well suited.

Life expectancy (battery life) is limited from roughly 8 to 10 years. When the operating temperature is above optimal or the discharge current is high, the life expectancy and the capacity begin to decline over time. The Gold Cap most appropriate when it is rarely discharged and used with low currents

Power supply TAMDL

The TPS62125 from Texas Instruments is a high efficiency synchronous step down converter optimized for low and ultra-low power applications providing up to 300 mA output current. It has a wide range of input voltages, from 3 V to 17 V, supports four cell alkaline, and 1 to 4 cell Li-Ion batteries in series configuration as well as 9 V to 15 V powered applications. The device includes a precise low power enabled comparator which can be used as an input supply voltage supervisor (SVS), which addresses system specific power up and down requirements. The standby current is 13 µA.

Jack connector as interface to a PC

For the development of the Timed Animal Manipulation Data Logger an Interface for connection to a computer is intended.
Through the data communication interface LEUART, which is
provided by the microcontroller EFM32G230 (chapter 1.2.4).
The jack connector is used to connect the signal of the LEUART interface with a PC. For this, a jack connector with 3.5 mm, found in many audio applications, is applied. Please regard a power supply of 3.3 V when buying cables.

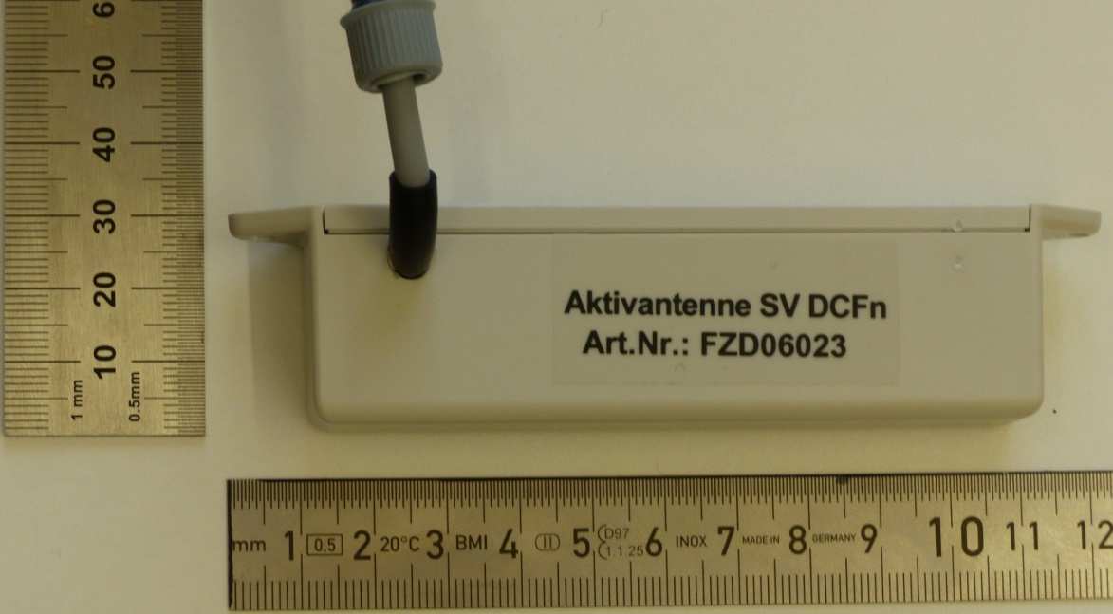
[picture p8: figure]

11.02.2019 | https://www.orn.mpg.de | Copyright 2019 ©, MPIO Seewiesen | page 19

Output voltages (Down converter)

The TPS62125 3.5 V - 42 V down converter from Texas Instruments is a highly efficient converter, which is optimized for low and ultra-low power applications of up to 2.5 A output current. If no load is recognised by the controller, the standby current is 138 µA. The controller is run by TAMDL in the Shutdown Mode. The Shutdown Current is 1.3 µA.

SD Memory Card Connector

The data from the RAM memory is stored in form of *.txt files on the SD-card, this is located in the SD Memory Card Connector. The size of the memory influences the energy consumption; the
smaller the memory size is, the smaller the energy consumption.
Therefore, it is recommended for the Timed Animal Manipulation
Data Logger (TAMDL) to use a small SD memory size of 2 GB. Larger memory sizes increase TAMDLs Energy consumption. Memory sizes are supported from only 2 GB up to 32 GB. Not every event is written onto the SD card immediately. It is first waited for the provided memory to be full. The writing on the SD card consumes quite some energy, which is why the access to the SD card should occur as rare as possible.

Hardware illustration radio clock receiver

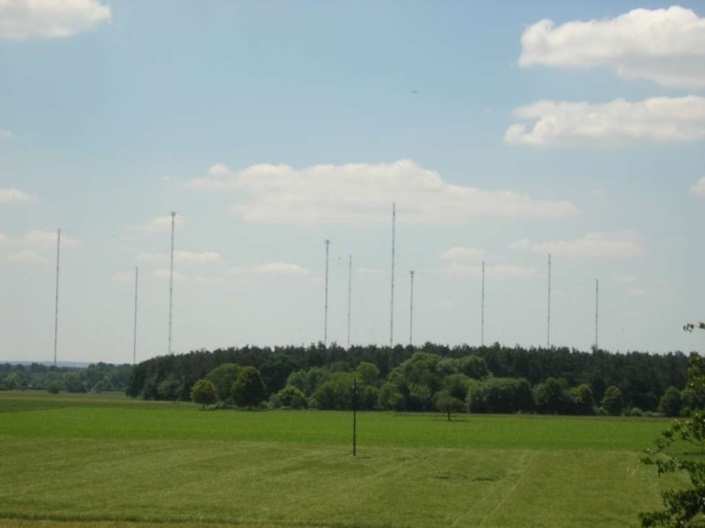
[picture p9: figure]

11.02.2019 | https://www.orn.mpg.de | Copyright 2019 ©, MPIO Seewiesen | page 20

Radio clock

The radio clock works in a similar way as a normal clock. In periodic intervals a signal to Europe from the long wave antenna in Mainflingen with a frequency of 77.5 MHz is received and synchronized. Long wave signals have been compared to short waves and medium waves, and have a relatively high range, making it is possible to receive the signal from Mainflingen with a range of up to 2000 km. On other continents, the time signals can be received as well, though with different frequencies.

The time of the radio clock is prompted every 24 hours by default and gets transferred to the clock of the MCU. A nonstandard detection takes place during a reset of the system or after energy supply has been restored, after the capacitor was discharged for too long to bridge power supply and in case of the voltage to come below 1.8 V.

The power supply of the clock is driven by the accumulator, which is also used for the other electric consumers and is described in chapter 1.7.

countries | designation | frequency
Germany | DCF | 77.5 kHz
France | TDF | 162 kHz
China | BPC | 68.5 kHz
Japan | JJY | 40 and 60 kHz
USA | WWVB | 60 kHz
Russia | Beta | 25 kHz
Great Britain | MSF | 60 kHz

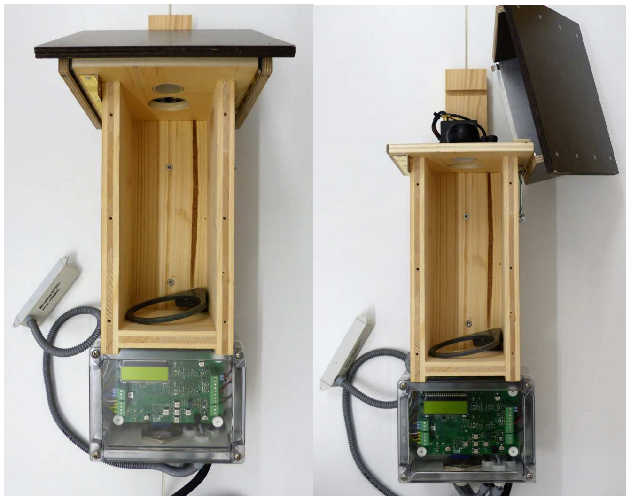
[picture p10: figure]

11.02.2019 | https://www.orn.mpg.de | Copyright 2019 ©, MPIO Seewiesen | page 21

## Smart Recorder (Hardware)

Peripheral devices are essential for the regular operation of the Timed Animal Manipulation Data Logger. Concerning the Smart Videotaping application these include an accumulator, a radio clock receiver, a RFID reader and a dashcam.

Hardware illustration

Outputs:

UA1 is the camera function which is in the top of the nestbox, using the configuration, the time at which the camera turns on and off can be manipulated.

UA2 is the RFID reader fitted to the bottom of the device and is either Short Range (SR) or Long Range (LR).

THREE POWER SOURCES- UA1, UA2 and BATTERY, determine the on and off times of the UA1, UA2, respective BATT and duration of on and off times and subsequent current and voltage measurements.

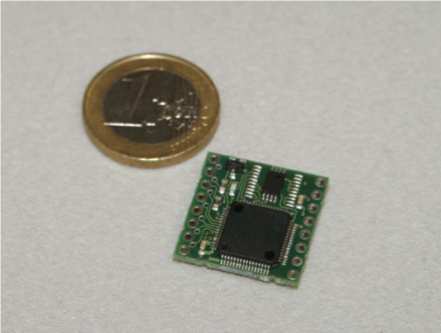
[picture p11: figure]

11.02.2019 | https://www.orn.mpg.de | Copyright 2019 ©, MPIO Seewiesen | page 22

RFID reader for transponders

RFID (radio-frequency identification) describes a technology for transceiver systems that uses automatic and non-contact identification and localisation of objects and living organisms with radio waves.

A RFID system consists of a transponder that is located on or within the object or living organism and contains an individual label and a reading device with an antenna for the readout of that label.

The coupling takes place via alternating magnetic fields produced by the reader within short range or via high frequency radio waves. Thereby, not only data is transmitted, but the transponder is also supplied with energy. Active transponders with a local power source are used to achieve longer ranges, but come along with higher expenses.

RFIDs are also used in other areas such as electronic locks and immobilizers, ski passes, cashless payment transactions and in libraries as theft protection.

The transponder frequency is not exactly the same as the RFID reader frequency. The RFID reader works with a frequency of 125 kHz and the transponder with 134.2 kHz. However, both systems are compatible and function together.

### 2.1.2.1 RFID receiver module

A RFID receiver module with a frequency of 125 kHz is used in the Smart Recorder application. The used receiver module from Elatec is designed with a small size, small price and versatile applications.

### 2.1.2.2 RFID antenna

The used RFID antenna has a diameter of 50 mm and is directly soldered on the RFID receiver module. If a voltage source is connected to the antenna, which is an

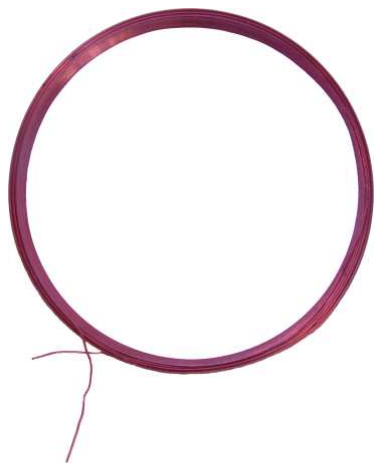
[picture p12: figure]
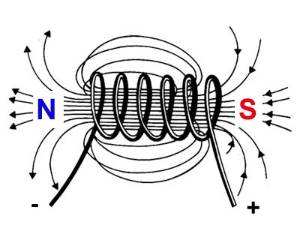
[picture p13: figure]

11.02.2019 | https://www.orn.mpg.de | Copyright 2019 ©, MPIO Seewiesen | page 23

air core coil with an inductivity of 490 µH and current begins to flow, an electric field is generated. The electric field is the energy source for the transponder.

If a transponder with its own antenna transmits a signal at a certain frequency, the RFID reader’s antenna collects the signal and transmits it.

### 2.1.2.3 RFID transponder

The used transponder is the highest performing passive transponder currently available on the market. These
transponders are encapsulated in biocompatible glass
and provide 100% unique identification. Because of the
small size of 8 mm x 1.4 mm and a very low weight of only 30 mg the tagged animals are minimally affected. So it is possible to tag even very small animals such as red ants.

The transponder contains a non-volatile flash memory. A combination of letters and numbers is stored on the flash memory during the production of the transponder.

The | transponders | are | known | as | FDX-B
MINIHPT8 and are made by the company
Biomark. The FDX-B indicates that the full duplex technique is used.

In duplex mode operating systems the electric
field is always present and the transponder sends its signal as soon as it enters the

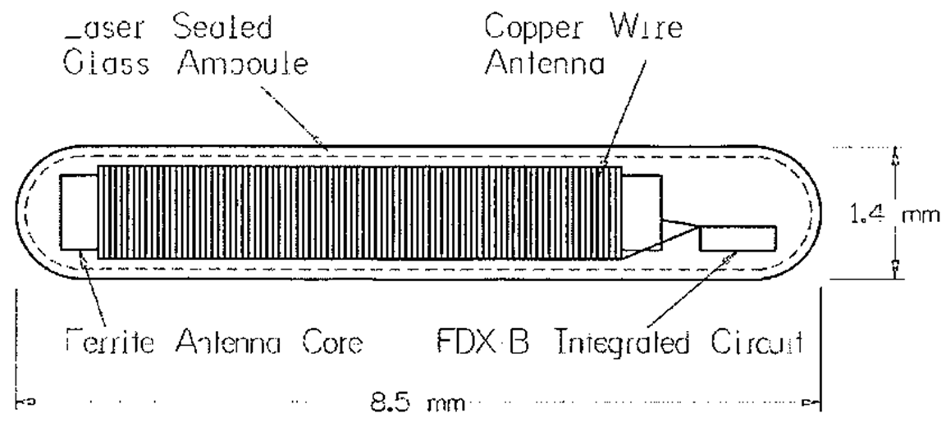
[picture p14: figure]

11.02.2019 | https://www.orn.mpg.de | Copyright 2019 ©, MPIO Seewiesen | page 24

reception area of the reader. The FDX transponder sends its ID continuously and can therefore be received relatively rapid.

11.02.2019 | https://www.orn.mpg.de | Copyright 2019 ©, MPIO Seewiesen | page 25

## Dashcam

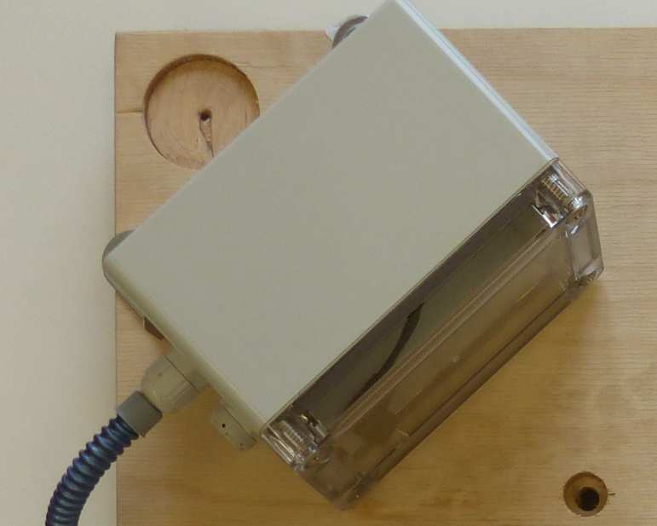
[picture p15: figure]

Video recording device with 12 V battery terminal.

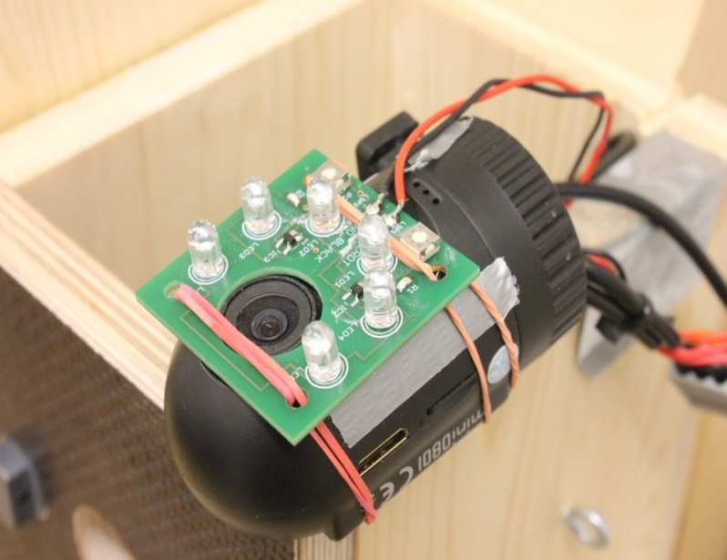
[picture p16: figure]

Housing for camera | Full HD Car DVR with GPS

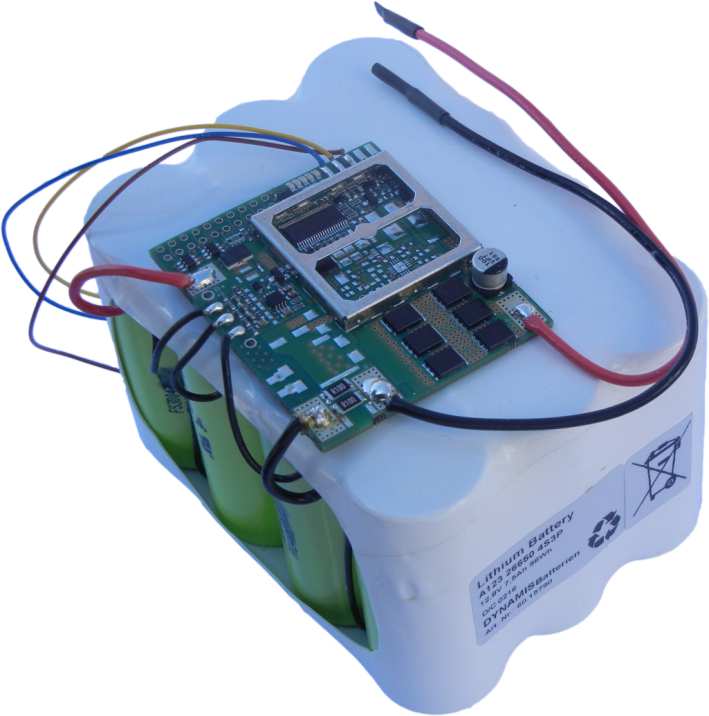
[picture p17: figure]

11.02.2019 | https://www.orn.mpg.de | Copyright 2019 ©, MPIO Seewiesen | page 26

## Accumulator

The lithium-ion battery from the company ‘Dynamis Batterien’ supplies
Timed | Animal | Manipulation | Data
Logger | (TAMDL) | with | electrical
energy. The capacity was chosen to ensure that there is enough energy to supply the Smart Recorder in a very active period for two weeks. Through the little specific energy of the lithium-ion battery of approximately 108 Wh/kg, the change of the accumulators is much less energy-sapping than with lead-acid batteries with a specific
energy of 30 - 60 Wh/kg.

The three LEDs on the accumulator’s board indicate the state of charge. One lit LED indicates that the accumulator is fully charged. Two LEDs indicate the accumulator is halfway charged. Three LEDs indicate an almost empty state of charge.

The lithium-ion battery has its own board, which can communicate with TAMDL via a bus system. Currently, the temperature of the accumulator, the capacitance values and the latest current drain of the Smart Feeder are prompted from TAMDL.

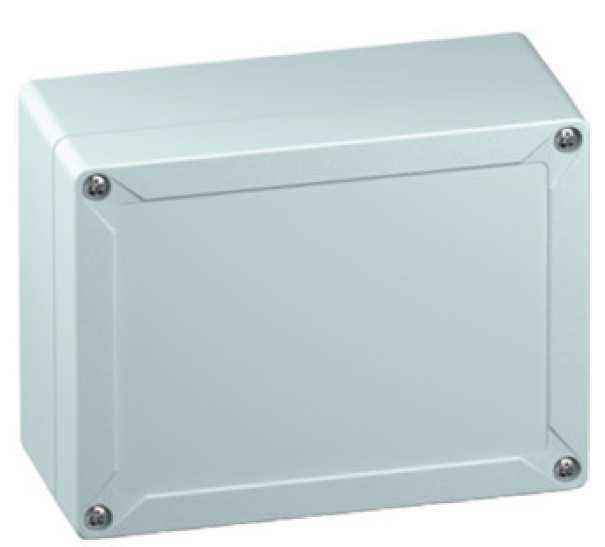
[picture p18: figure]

11.02.2019 | https://www.orn.mpg.de | Copyright 2019 ©, MPIO Seewiesen | page 27

## Housing

Housing for the main board

The housing from the main board consists entirely of opaque polycarbonate. The lid is lockable with bayonet locks which are quick and easy to use. The screws are secured from falling, preventing any loss.

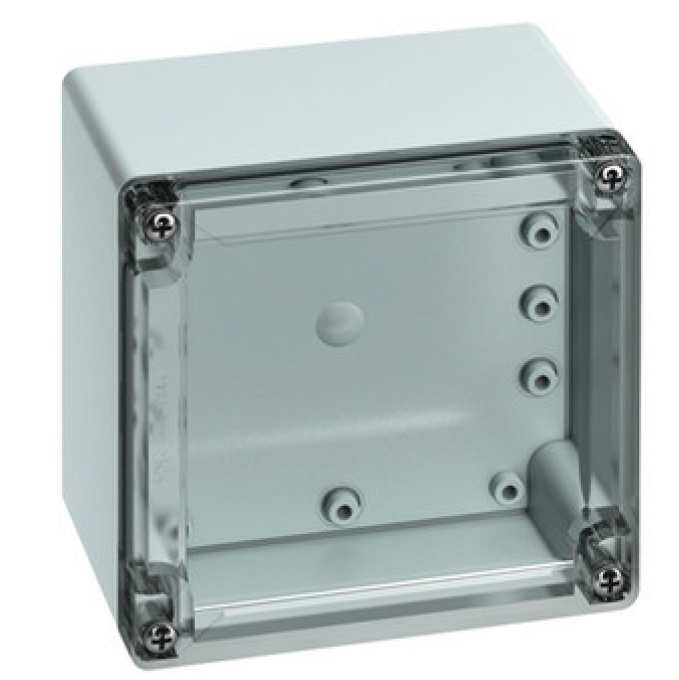
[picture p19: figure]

11.02.2019 | https://www.orn.mpg.de | Copyright 2019 ©, MPIO Seewiesen | page 28

Housing for the accumulator

The housing of the accumulator consists entirely of polycarbonate with the lid being made of transparent polycarbonate, so that there is no need to open the lid in order to see the LEDs. The lid is lockable with bayonet locks as well. The same screws are used here and are also secured against falling out.

11.02.2019 | https://www.orn.mpg.de | Copyright 2019 ©, MPIO Seewiesen | page 29

## General working conditions

Component designation | Timed Animal Manipulation Data Logger Smart Feeder Application
Manufacturer | MPIO http://www.orn.mpg.de/
Dimensions main board (L X B x H) | 121 mm x 81 mm x 1,5 mm
Overall temperature range | -10°C to 70°C (DCF77)
Storage temperature range | -20°C to 60°C
Overall moisture | Relative moisture 35% to 85% (at 5 to 35°C)

Detailed information, in particular concerning the electrical properties of the Timed Animal Manipulation Data Logger can be found in the datasheet.

The working conditions from single devices can be found in the datasheets in chapter 8.

11.02.2019 | https://www.orn.mpg.de | Copyright 2019 ©, MPIO Seewiesen | page 30

## Energy supply

The Timed Animal Manipulation Data Logger (TAMDL) is especially designed to have low energy requirements. The electrical power requirements are explained more precisely in this chapter.

The EFM32G230 has five different economical energy modes, where only two of which are used for TAMDL. These are the Deep Sleep Mode and the Sleep Mode whereby the Sleep Mode is the Active Mode and the Deep Sleep Mode is the Inactive Mode. In these energy modes different consumers are active. The Smart Feeder application of the Timed Animal Manipulation Data Logger switches between the Active Mode and the Inactive Mode through light barrier activity. If the RFID reader and the light barrier detect no activity for 6 minutes, the Smart Recorder switches into the Inactive Mode again to save energy.

The energy-intensive consumers, like the RFID reader, are only supplied with electrical Energy when required. The RFID reader is the largest consumer of electrical energy in the Smart Feeder application, when no camera is connected.

Electrical properties and, to some extent, battery drain, can be drawn from the datasheets of the built-in components. The datasheets are linked in chapter 8.

In the following sections, the current supply and the voltage supply will be examined separately.

11.02.2019 | https://www.orn.mpg.de | Copyright 2019 ©, MPIO Seewiesen | page 31

## Current supply

ARM Cortex Processor

From the five available modes of operation only the Deep Sleep Mode and the Sleep Mode are used.

### 0.9 μA @ 3 V Deep Sleep Mode, including Real Time Clock with 32.768 kHz

Oscillator, Power-on Reset, Brown-out Detector, RAM and CPU retention

### 45 μA/MHz @ 3 V Sleep Mode

RFID

RFID on measured: 35,4mA

RFID off measured: 1,36mA

(from schematics)

Radio clock

The clock of the microcontroller is updated at a certain time every night through the time signal from Mainflingen. The radio time will be also updated when the system is reset.

Nominal current 100µA | Quiescent current 5 µA

LED

Each LED has an electric current demand of 2 m. There are two built-in LEDs.

11.02.2019 | https://www.orn.mpg.de | Copyright 2019 ©, MPIO Seewiesen | page 32

Accumulator LEDs and self-discharge

LEDs | electric current demand
Without | 271 µA
Only LED1 | 308 µA
LED1 + LED2 | 343 µA
LED1 + LED2 + LED3 | 384 µA

The self-discharge by lithium-ion-batteries at 20°C is less than 2% per month.

Overview of the nominal currents

This table contains the maximum current demands of the most important devices. If all are active at the same time, the current demand behind the down converter at

### 3.3 V is 51 mA and with that the maximum power input before the down converter

is around 0.1683 W.

devices | currents
RFID | 35.4 mA
2* LED | 2 x 2 mA
ARM Cortex M3 | 45 µA/MHz (1.44 mA)
radio clock | 0.1 mA
light barriers | 2x 120 µA
Total current behind the down converter with 3.3V | 42.2 mA (When all consumers are active at the same time without down converter losses)
Total input in front of the down converter with 12.8 V | 155 mW (When all consumers are active at the same time with down converter losses)

11.02.2019 | https://www.orn.mpg.de | Copyright 2019 ©, MPIO Seewiesen | page 33

Overview of the currents in the different operating modes

| Shutoff Mode | Stop Mode | Deep Sleep Mode | Sleep Mode | Run Mode
RFID | Not used | Not used | Off | Can be on | Not used
ARM Cortex M3 | Not used | Not used | On | On | Not used
Radio clock | Not used | Not used | Can be on | Can be on | Not used
LEDs | Not used | Not used | Can be on | Can be on | Not used
Light barrier | Not used | Not used | On | On | Not used
Down converter | Not used | Not used | On | On | Not used
Accumulator board | Not used | Not used | On | On | Not used

11.02.2019 | https://www.orn.mpg.de | Copyright 2019 ©, MPIO Seewiesen | page 34
| Deep Sleep Mode (inactive mode) | Sleep Mode (active mode)
RFID (with 3.3 V) | 0 | On (35.4mA)
ARM Cortex M3 (with 3.3 V) | 0.9 µA | 45 µA/MHz (1.44 mA)
Radio clock (with 3.3 V) | 0.1 mA (once a day for approx. 5 min; also at reset and start) | 0.1 mA (once a day for approx. 5 min; also at reset and start)
LED (with 3.3 V) | 2 mA (2 units if on) | 2 mA (2 units if on)
Down converter (3.3 V) | 13 μA | 13 μA
Total current behind the down converter (without down converter losses and 3.3 V) | 0.0609 mA (2 x light barriers and MCU) | 36.88 mA (RFID active, MCU active, light barriers, down converter)
Total input behind of the down converter (without down converter losses and 3.3 V) | 0.0609 mA x 3.3 V = 0.000201 W = 201 x 10^-6 W | 36.88 mA x 3.3 V = 0.122 W
Total input in front of the down con-verter (with down converter losses and 12.8 V) | (with η = 50%) 0.000201W/0.5 = 0.000402 W = 402 x 10^6 W | (with η = 90%) 0.122 /0.9 = 0.136 W
Total current in front of the down converter (with down converter losses 12.8 V) (theoretical) | (with η = 50%) 0.0314 mA | (with η = 90%) 10.6 mA
Measured total current in front of the down converter (with down converter losses 12.8 V) (real) | 0.22 mA = real measured inactive mode (connected radio clock but inactive, controller in Deep Sleep Mode, Gold Cap, connected LED but off, buttons, down converter) | 11 mA = real measured active mode (connected radio clock but inactive, controller, LED connected but off, gold cap, SD card, down converter, light barrier, RFID on)
Accumulator board with LEDs current demand | (0.271 mA – 0.384 mA) | (0.271 mA – 0.384 mA)
Total current with accumulator board | 0.3024 mA – 0.4154 mA | 10.87 mA – 10.98 mA
Total Input ink. accumulator board with 12.8 V (theoretical) | 0.00387 W – 0.00532 W | 0.139 W – 0.141 W
Total Input with measured value + theoretically accumulator board de-mand with 12.8 V (real) | 0.028 W – 0.0158 W | 0.141 W – 0.142 W

## Voltage supply

11.02.2019 | https://www.orn.mpg.de | Copyright 2019 ©, MPIO Seewiesen | page 35

All consumers are supplied with 3.5 Volts, which are provided by the down converter from the 12.8 Volts from the lithium-ion-accumulator. An input voltage of 5 V for the down converter is sufficient.

## Electrical energy storage

The main power supply is ensured by the lithium-ion-accumulator. If the accumulator is removed, a capacitor ensures the supply.

Accumulator

If the whole capacity of a lithium-ion-accumulator is completely used it can have negative effects on the lifetime of the accumulator. Therefore, a certain percentage of the total capacity is not used. The accumulator of the Animal Presence RFID Data Logger uses 83% of the total capacity.

Roughly 17 % of the capacity of the accumulator is not used.

voltage | 12.8 V
nominal capacity | 7.5 Ah
total capacity | 8.97 Ah
stored energy | 96 Wh

The lithium-ion-accumulator has its own board, which is able to communicate with the Animal Presence RFID Data Reader via a data bus.

Capacitor

If the energy supply from the accumulator is no longer available, a capacitor with

### 0.22 farad ensures the energy supply. The stored energy is enough to supply

TAMDL for around 30 seconds. During the discharge, the voltage of the capacitor declines from 3.6 Volts to 1.8 Volts.

11.02.2019 | https://www.orn.mpg.de | Copyright 2019 ©, MPIO Seewiesen | page 36

Conversion losses

The accumulator provides electrical energy with a voltage of 12.8 Volts. The EFM32G230 and other consumers require a significantly smaller voltage of around

### 3.3 Volts. This reduction of voltage is achieved by a down converter which is

described in chapter Fehler! Verweisquelle konnte nicht gefunden werden.. The down converter doesn’t work with transformers but with resistors.

Range estimation of the accumulator

Range at maximum power (If the Timed Animal Manipulation Data Logger is always active and there is no maintenance, RFID) | 96 Wh / 0.142 W = 676 hours = 28.16 days
Range at minimum power (The Timed Animal Manipulation Data Logger is in the Deep Sleep Mode and there is no maintenance; radio clock and RFID off, 1x light barrier) | 96 Wh / 0.0058 W = 16552 hours = 690 days = 1.889 years

The value for the range at minimum power can only theoretically be achieved. In reality the self-discharge causes the accumulator to be discharged earlier. Moreover, an inactivity of more than two years is not intended for the application.

11.02.2019 | https://www.orn.mpg.de | Copyright 2019 ©, MPIO Seewiesen | page 37

## Operation of the Smart Recorder

The operation of the Timed Animal Manipulation Data Logger (TAMDL) with the Smart Feeder application will be explained in this chapter. This includes the information detailing accumulator replacement, SD card change, software updates, the loading of the accumulator and troubleshooting.

Menu Display

The menu display on the TAMDL firmware display shows the time, and all temporary messages such as SD insertion/removal or the registering of a transponder ID. It also allows the calibration of voltage and current to be measured of the UA1 and UA2.

The default screen (Home screen) shows the actual time in the first line and an „Info-Area“ in the second line of the LCD. All temporary messages are displayed there, e.g. when an SD-Card is inserted or removed. Transponder IDs are also displayed here.

After some time of inactivity or when asserting the Set-Key for more than 750ms, the menu returns to the home screen.

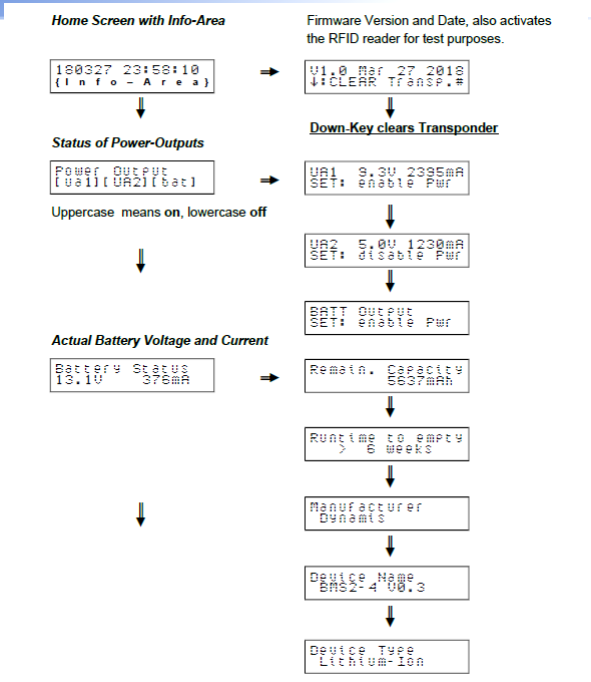
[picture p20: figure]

11.02.2019 | https://www.orn.mpg.de | Copyright 2019 ©, MPIO Seewiesen | page 38

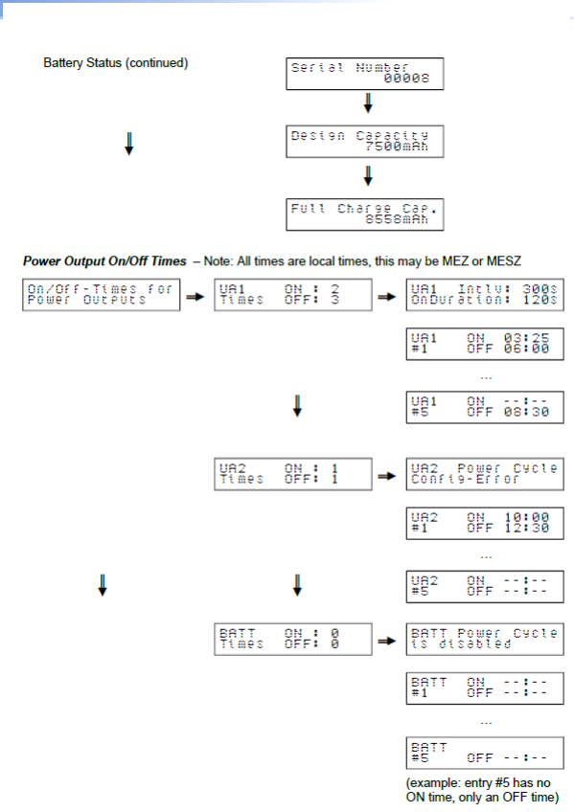
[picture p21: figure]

11.02.2019 | https://www.orn.mpg.de | Copyright 2019 ©, MPIO Seewiesen | page 39

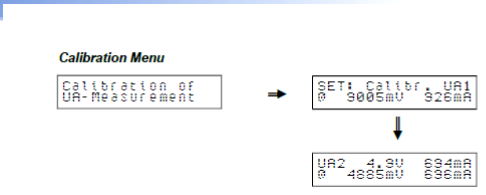
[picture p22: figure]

11.02.2019 | https://www.orn.mpg.de | Copyright 2019 ©, MPIO Seewiesen | page 40

Calibration Procedure

To calibrate the voltage and current measurement channels of the power outputs UA1 and UA2, follow these steps:

- Connect a constant load to UA1, and also a voltage and a current meter.
- Go to the calibration main menu, then further to the sub-menu for UA1. At this time the message UA1 CALIBRATION IS NOT POSSIBLE may be displayed if no calibration reference values exist in the configuration file, but this is not a problem.
- As long as you remain in this sub-menu, the respective power output is activated and you could measure voltage and current for this specific load.
- Write these values in the CONFIG.TXT file on an SD-Card. The variable names are

UA1_CALIBRATE_mV and UA1_CALIBRATE_mA. After that, insert the SD-Card
into the TAMDL board.
- The configuration file is read and the two values will be displayed.
- Verify if the voltage and current values are still valid, then assert the Set-Key to start calibration.
- The conversion factors will be calculated and the display now shows the actual voltage and current values together with the reference values.

11.02.2019 | https://www.orn.mpg.de | Copyright 2019 ©, MPIO Seewiesen | page 41
- Proceed in the same way with UA2 by asserting the Down-Key to enter its sub-menu.
- After both channels have been calibrated, return to the calibration main menu by asserting the Left-Key. This will save the conversion factors to flash memory, so they can be loaded during the next start-up.
- If unsure you could abort this procedure by asserting the Set-Key for more than 750ms. The menu returns to the home screen and the power outputs are disabled.

Configuration

The configuration file allows you to change the voltage, time and activation of all outputs in the device. For example, setting the UA1 (camera) to turn on for 2 hours during the night and 4 hours during the day. This allows for flexibility, whereby the device can be set in advance without the need to set it each day.

## Accumulator replacement

The accumulator has to be replaced in periodic intervals. The range of an accumulator depends on several factors, including ambient temperature, activity of the Smart Feeder and therefore energy demand of the Smart Feeder. The activity usually depends on the season of the year. As birds have a higher level of activity near the Smart Feeder (SF) during the breeding season, the SF is often in the active mode and needs much more energy than during other seasons.

Reasons for accumulator replacement

The accumulators have boards with three LEDs which indicate the state of charge. If three LEDs are blinking this shows that the accumulator is almost empty and should be exchanged as soon as possible. When two LEDs are blinking the accumulator is half full and one LED blinking indicates an almost full accumulator. If there are no LEDs blinking the accumulator is completely empty and no longer able to supply energy.

When all LEDs are lit permanently this indicates a defect at the accumulator or at the accumulator board. In this case the whole accumulator needs to be changed.

11.02.2019 | https://www.orn.mpg.de | Copyright 2019 ©, MPIO Seewiesen | page 42

Placement of the accumulator

The wind and therefore also rain, snow and mist in Europe primarily come from the west. This can be seen visibly on trees where the western-facing sides are often moss-covered. Therefore, placement of the accumulator on the eastern side can minimize the possibility of damage due to oxidation.

Moreover, the accumulator can be placed in a way that water can drain away at an edge and does not accumulate at the connector or at the cable input.

If the accumulator becomes warm, it can age more rapidly or be damaged. The operating temperature range of the accumulator is between minus 30°C and 55°C according to manufacturer specifications. When the sun shines directly on the accumulator it is possible to exceed this range. Therefore, the accumulator should be protected against direct sunlight through e.g. placement on the north-facing side of a tree or by shading it in another way.

When placing the accumulator, one should be aware of these external environmental influences and place the accumulator appropriately, because of the high costs of the accumulators.

## SD card change

The SD cards have a large memory size so that the memory may be filled only after several months or even years.

As continuous recording of data is desired and as unexpected malfunctions of the Smart Feeders are always a possibility, they should be visited and controlled regularly every couple of weeks. In doing so, SD cards can be exchanged and stored data can be checked. If there is unusual data on the SD cards, it could indicate a malfunction of the Smart Feeder. In this case, a maintenance should be arranged.

11.02.2019 | https://www.orn.mpg.de | Copyright 2019 ©, MPIO Seewiesen | page 43

## Software update

There are three possible methods to write software code on to the flash memory. The debug probe method from IAR systems and the debug interface method without debug probe are always possible. If software has already been written on the flash memory by either of these methods, an additional method using SD cards is also available.

The microcontroller EFM32G230 contains a flash memory with a memory size of 128 KB. This memory contains the software by which the microprocessor works. 128 KB of memory is a sufficient size for operation, even with very complicated applications of the Timed Animal Manipulation Data Logger. Update possibilities are described in more detail in chapter 7.1.

## Loading the accumulator

The accumulators should be changed and charged in regular intervals. The accumulator has to be visually checked for damage when it is changed.

Recharger

Device description | Mascot type 2541 Li, 4 cell, 2A, Lithium Ion Battery Charger, 35W
Manufacturer | Mascot http://www.mascot.no/home/
Nominal power | 35 W
Battery voltage | 12V
Charging current | Up to 2 A
Recommended battery capacity | 1 – 10 Ah
Loadable cells | 4
Charging characteristic | IUoU

The charge process is separated in to three sections.

### 1. Charging current is 2 A until the voltage reaches 14.7 V

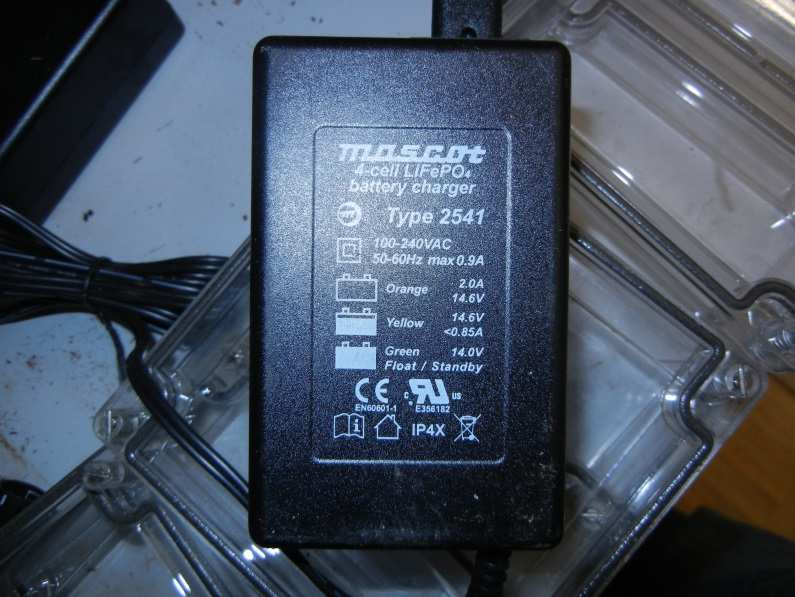
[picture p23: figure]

11.02.2019 | https://www.orn.mpg.de | Copyright 2019 ©, MPIO Seewiesen | page 44

### 2. Voltage will be held at 14.7 V; current declines slowly 3. A yellow display shows that the charging current declined beneath 1 A

4. If the charging current is below 250 mA the recharger switches off.

### 5. In the maintenance charging module the accumulator voltage will be kept at

13.7 V.

Charging method IUoU

IUoU means that the initial charging current is constant similar to the CCCV charging method until the final charging voltage is reached. Then the voltage is held at the charging end voltage. This constant high voltage can be harmful for the accumulator and reduce the capacity. Therefore, the voltage will be reduced after a certain amount of time; with that the maintenance charging is initiated. With the reduced voltage the accumulator can be charged permanently and the amount of current is roughly like the self-discharge. The ‘I’ in IUoU stands for constant current, ‘Uo’ stands for constant voltage with charging end voltage and ‘U’ for reduced constant Voltage

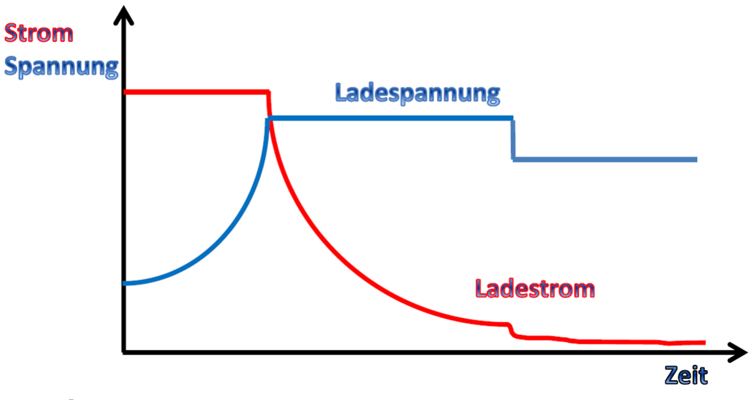
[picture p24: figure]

11.02.2019 | https://www.orn.mpg.de | Copyright 2019 ©, MPIO Seewiesen | page 45

Charge time

The accumulators can be charged in roughly one day to ensure that the accumulators are securely fully-loaded.

Theoretically, a charging time of roughly 3 hours in both rechargers is enough for a complete loading.

The charging time at the IUoU can be marginally less, because the Uo phase at constant voltage with end-of-charge voltage can be higher than the CV voltage at the CCCV method.

### 7.5 Ah / 2A = 3.75 h

A discharged accumulator with 7.5 Ah requires a charging current of 2A for more than 3.75 hours, because the loading does not take place with a maximal current of 2A the whole time.

## Troubleshooting Smart Feeder

The current version of the Smart Feeder has taken three years of development. Some malfunctions could be encountered and thus lead to experience in troubleshooting and development of specific procedures for malfunctions which may be detected.

11.02.2019 | https://www.orn.mpg.de | Copyright 2019 ©, MPIO Seewiesen | page 46

Troubleshooting in the field

The field troubleshooting takes place after a malfunction is detected through information from the data collected in the SD cards. Incorrect data indicates a malfunction at the Smart Feeder.

Troubleshooting in the laboratory

Via the LEUART-interface the Smart Feeder can be connected to a PC. This makes it possible to transfer information transmitted by the Microcontroller. This allows for a detailed view into the Smart Feeder.

If the failure cannot be detected via the LEUART-interface, the Smart Feeder has to be measured electronically for further troubleshooting.

11.02.2019 | https://www.orn.mpg.de | Copyright 2019 ©, MPIO Seewiesen | page 47

## Software

The Software on the flash memory in the Timed Animal Manipulation Data Logger is programmed with the programming language C. This software is diverse for different applications and has to be regenerated for every application. It needs to be smaller than 128 KB for the flash memory. The software for the Smart Feeder application will be described in this chapter. It includes reset options, the reset process, how data is stored and what occurs when the SD card is changed. Also described is how regular queries are stored, what can be done with the built-in buttons on the board and the possibility of software updates.

## Reset

The reset can be used to restart the system of the Timed Animal Manipulation Data Logger when an unknown failure occurs. The procedure for a reset is always the same. The reset is a new start and can be compared with the start of a PC.

Possibilities to perform a manual reset

The Timed Animal Manipulation Data Logger can be restarted manually in two ways:

- Via pushbutton
- Reset after electrical energy was not available for considerable time, so that

the capacitor could not provide enough energy. The capacitor has enough energy to provide TAMDL for approx. 3 min.

Procedure after reset

After a reset the following procedure takes place:

### 1. Both LEDs (red and orange) will be illuminated to show that the hardware or

software is active and the LEDs are working.

11.02.2019 | https://www.orn.mpg.de | Copyright 2019 ©, MPIO Seewiesen | page 48

Only visible in a terminal program on a PC.

### 2. In case a SD card is recognised, its data system is mounted and the free space

on the memory is displayed. This takes place at every exchange of SD cards during operation.

### 3. Afterwards it will be searched for a log file with the name ‘BOXnnnn.TXT’ (nnnn

is a random decimal number). In case the file exists on the SD card, the name will be displayed on the LC display; otherwise the file ‘BOX0999.TXT’ will be created.

Furthermore, the DCF77 module is switched on to receive date and time. The red LED now flashes to the rhythm of the radio clock signal.

4. After date and time got synchronized, the red LED switches off.

Reset protocol

If a start or a reset of the Timed Animal Manipulation Data Logger is carried out some protocol lines are written on the SD card to comprehend the process of the maintenance.

20190107-150721.183 SD-Card Removed

20190107-150722.135 SD-Card Inserted

20190107-150722.215 SD-Card Initialized

20190107-150722.215 SD-Card File System mounted

20190107-150722.468 SD-Card 1853MB free

20190107-150722.470 Media Change: BOX0999.TXT -> BOX0999.TXT

20190107-150722.497 MCU: EFM32G230F128 HW-ID: 0x247DBC085A3E2629

20190107-150722.528 Battery Manufacturer Name : | Dynamis
20190107-150722.554 Battery Manufacturer Data : | 61.90002/15790
20190107-150722.580 Battery Device Name | : | BMS2-4_V0.3
20190107-150722.605 Battery Device Type | : | Lithium-Ion
20190107-150722.612 Battery Serial Number | : 00008
20190107-150722.619 Battery Design Voltage | : 3.300V per cell
20190107-150722.625 Battery Design Capacity | : 7500mAh

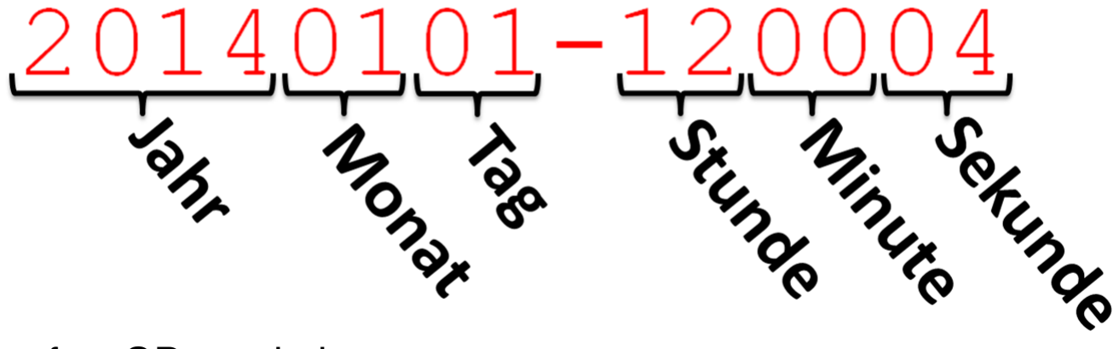
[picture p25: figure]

11.02.2019 | https://www.orn.mpg.de | Copyright 2019 ©, MPIO Seewiesen | page 49

20190107-150722.632 Battery Full Charge Capac.: 8198mAh

20190107-150723.220 Battery Remaining Capacity: 3017mAh

20190107-150723.229 Battery Runtime to empty | : 1160min (0d)
20190107-150723.237 Battery Actual Voltage | : 13.1V
20190107-150723.243 Battery Actual Current | : | 156mA

20190107-150723.483 Reading Configuration File CONFIG.TXT

## Data storage

All important information from the RAM memory will be saved in a txt-file on the SD card. Every event or stored message begins with the date and time of the event.

Following the date and time there is a blank space. Then follows the actual status message

Procedure after SD card change

After a new SD card is plugged in the following procedure starts.

1. It displays that a new SD card has been detected.

20190107-150722.135 SD-Card Inserted

20190107-150722.215 SD-Card Initialized

20190107-150722.215 SD-Card File System mounted

11.02.2019 | https://www.orn.mpg.de | Copyright 2019 ©, MPIO Seewiesen | page 50
2. The following line shows how much free space remains on the SD card.

20190107-150722.468 SD-Card 1853MB free

### 3. Afterwards it will search for a log file with the name ‘BOXnnnn.TXT’ (nnnn is a

random decimal number). In case that the file exists on the SD card the name will be displayed on the LC display otherwise the file ‘BOX0999.TXT’ will be created.

20190110-133618.338 Using Filename BOX0999.TXT

20190110-133618.338 Media Change: BOX0999.TXT -> BOX0999.TXT

### 4. The hardware ID will be displayed, which is a unique number allocated to each

Timed Animal Manipulation Data Logger

20190110-133618.363 | MCU: | EFM32G230F128 | HW-ID:

0x247DBC085A3E2629

### 5. The status of the accumulator is then displayed, including the manufacturer

name, manufacturer data, device name, device type, serial number, design voltage, design capacity, total capacity, remaining capacity, remaining time at actual current and at least the measured actual voltage.

20190110-133618.394 Battery Manufacturer Name : | Dynamis
20190110-133618.420 Battery Manufacturer Data : | 61.90002/15790
20190110-133618.445 Battery Device Name | : | BMS2-4_V0.3
20190110-133618.470 Battery Device Type | : | Lithium-Ion
20190110-133618.477 Battery Serial Number | : 00008
20190110-133618.483 Battery Design Voltage | : 3.300V per cell
20190110-133618.490 Battery Design Capacity | : 7500mAh

20190110-133618.497 Battery Full Charge Capac.: 7811mAh

20190110-133619.088 Battery Remaining Capacity: 7811mAh

20190110-133619.096 Battery Runtime to empty | : More than 6 weeks
20190110-133619.103 Battery Actual Voltage | : 13.4V
20190110-133619.110 Battery Actual Current | : | 5mA

11.02.2019 | https://www.orn.mpg.de | Copyright 2019 ©, MPIO Seewiesen | page 51
6. The configuration file CONFIG.txt is read.

RFID_TYPE [SR, LR]
RFID reader device type: SR is Short Range reader, LR is Long Range reader. If no type is specified (i.e. the variable is #-commented), the associated
logic will not be activated.

RFID_POWER [UA1, UA2, BATT]
RFID reader power source, must be set to UA1 or UA2.
If no value is specified (i.e. the variable is #-commented), the associated logic will not be activated.

RFID_ABSENT_DETECT_TIMEOUT [s]
An RFID reader regularly re-sends the ID, as long as the transponder can be received. This is used to retrigger a "still present" timer. The value specifies the time in seconds, after which the transponder is treated as "absent" when its ID could not be received again.
A value of 0 disables the absent logic. This is useful for "fly thru" designs, e.g. with the Smart Nest Box.

UA1_ON_TIME_1~5,UA1_OFF_TIME_1~5,UA2_ON_TIME_1~5, UA2_OFF_TIME_1~5,
BATT_ON_TIME_1~5, BATT_OFF_TIME_1~5 [hour:min] MEZ
These variables determine the on and off times of the UA1, respective UA2 power output. If an RFID reader is assigned to an output, the UART will be activated additionally.
UA1_INTERVAL, | UA1_ON_DURATION, | UA2_INTERVAL,
UA2_ON_DURATION, BATT_INTERVAL and BATT_ON_DURATION in [s] These optional variables allow you to define a Power Cycle Interval within
the on times of the respective power output. XXX_INTERVAL specifies the interval in seconds, XXX_ON_DURATION the power ON duration in seconds within this interval.
The OFF duration is calculated XXX_INTERVAL minus XXX_ON_DURATION. There exists only one set of values per output. These are applicable for
all five on/off-times.

UA1_MEASURE_FOLLOW_UP_TIME, UA2_MEASURE_FOLLOW_UP_TIME, and

11.02.2019 | https://www.orn.mpg.de | Copyright 2019 ©, MPIO Seewiesen | page 52

BATT_MEASURE_FOLLOW_UP_TIME [s]
Duration in [s], the measurement of the respective power output is still performed. Additionally, BATT_INP voltage and current is measured via the battery controller. For the BATT output, only BATT_INP is measured. UA1_CALIBRATE_mV, UA2_CALIBRATE_mV [mV]
Calibration reference voltage for UA1 and UA2, specified in [mV].

UA1_CALIBRATE_mA, UA2_CALIBRATE_mA [mA] Calibration reference current for UA1 and UA2, specified in [mA].

# Calibration values for UA1 and UA2 measuring

UA1_CALIBRATE_mV | = 9100
UA1_CALIBRATE_mA | = 228
UA2_CALIBRATE_mV | = 0
UA2_CALIBRATE_mA | = 0

# RFID configuration

RFID_TYPE | = LR
RFID_POWER | = UA1
RFID_ABSENT_DETECT_TIMEOUT = 5

# Follow-up times after measurement [s] UA1_MEASURE_FOLLOW_UP_TIME = 2 #UA2_MEASURE_FOLLOW_UP_TIME = 0 #BATT_MEASURE_FOLLOW_UP_TIME = 0

# Operating times for UA1 output [hour:min] MEZ

UA1_ON_TIME_1 | = 08:00
UA1_OFF_TIME_1 | = 18:00

# Power Cycle Interval for UA1 output [s]

UA1_INTERVAL | = 20 # 10sec Interval
UA1_ON_DURATION | = 10 # 5sec.On Duration

# Operating times for UA2 output [hour:min] MEZ

#UA2_ON_TIME_1 | = 00:00

#UA2_OFF_TIME_1 | = 00:00

# Power Cycle Interval for UA2 output [s]

11.02.2019 | https://www.orn.mpg.de | Copyright 2019 ©, MPIO Seewiesen | page 53
#UA2_INTERVAL | = 20

#UA2_ON_DURATION | = 10

# Operating times for BATT output [hour:min] MEZ

#BATT_ON_TIME_1 | = 00:00

#BATT_OFF_TIME_1 | = 00:00

# Power Cycle Interval for BATT output [s]

#BATT_INTERVAL | = 20

#BATT_ON_DURATION | = 10

20190110-133619.356 Reading Configuration File CONFIG.TXT

### 7. The time of the microcontroller is updated through the signals from the radio

clock. This process usually only takes a few minutes.

20140101-120120.205 DCF77: Time Frame 1 is 20190110-132800

20140101-120220.205 DCF77: Time Frame 2 is 20190110-132900

20190110-132900.207 Initial Time Synchronisation

20190110-132900.000 DCF77: Time Synchronization 13:29:00 (MEZ)

20190110-132900.001 DCF77: Disabled

11.02.2019 | https://www.orn.mpg.de | Copyright 2019 ©, MPIO Seewiesen | page 54

## Periodic routine queries

Time update

Every 24 hours, during the night the time from the microcontroller is updated by the signals from the radio clock.

20190107-015500.000 DCF77: Enabled

20190107-015800.001 DCF77: Time Frame 1 is 20190107-015800

20190107-015900.001 DCF77: Time Frame 2 is 20190107-015900

20190107-015900.000 DCF77: Time Synchronization 01:59:00 (MEZ)

20190107-015900.000 DCF77: Disabled

Further outputs:

Log ("DCF77: Changing time zone from MEZ to MESZ");

Log ("DCF77: Changing time zone from MESZ to MEZ”);

If the DCF77 is not connected, there is no sync signal and no synchronisation.

Battery status query

At 11 a.m. and 11 p.m. the battery status is written on the memory as well as on the SD card. In addition, the current power demand is calculated. The range of the accumulator is calculated from data taken from the accumulator board. The remaining capacity and the current power demand are used for the calculation of the remaining range.

20190110-133619.088 Battery Remaining Capacity: 7811mAh

20190110-133619.096 Battery Runtime to empty | : More than 6 weeks
20190110-133619.103 Battery Actual Voltage | : 13.4V
20190110-133619.110 Battery Actual Current | : | 5mA

11.02.2019 | https://www.orn.mpg.de | Copyright 2019 ©, MPIO Seewiesen | page 55

## Recorded events

One task of the Timed Animal Manipulation Data Logger is to record the behaviour of animals. In the Smart Feeder application this is achieved via recordings from the light barrier activity and transponder detections as well as via the closing of the shutter.

Timer

UA1_ON_TIME_1~5,UA1_OFF_TIME_1~5,UA2_ON_TIME_1~5, UA2_OFF_TIME_1~5,BATT_ON_TIME_1~5, BATT_OFF_TIME_1~5 [hour:min] MEZ
These variables determine the on and off times of the UA1, respective UA2
power output. If an RFID reader is assigned to an output, the UART will be activated additionally.

20190110-141100.001 Power Output UA2 enabled

20190110-141100.001 ADC is switched ON

20190110-141100.105 UA2 | : | 5.0V | 1mA
20190110-141100.217 BATT_INP: 13.4V | 1mA
20190110-141100.362 UA2 | : | 5.0V | 29mA
20190110-141100.732 BATT_INP: 13.4V | 1mA

20190110-141136.653 Transponder: 4B76C4B43A6F0001

20190110-141213.000 Transponder: 4B76C4B43A6F0001 ABSENT

20181218-124555.000 Power Output UA2 disabled

20181218-124555.000 RFID is powered off

11.02.2019 | https://www.orn.mpg.de | Copyright 2019 ©, MPIO Seewiesen | page 56

Standard recording

In the following there are typical status messages:

20181122-152253.826 Power Output UA1 enabled

20181122-152253.853 UA1 | : | 0.0V | 434mA

20181122-152253.956 BATT_INP: Battery Controller Read Error

20181122-152253.956 UA1 | : | 5.0V | 515mA
20181122-152254.059 UA1 | : | 5.0V | 461mA
20181122-152254.162 UA1 | : | 5.0V | 513mA
20181122-152254.368 UA1 | : | 5.0V | 531mA

20181122-152254.470 BATT_INP: Battery Controller Read Error

20181122-152254.882 UA1 | : | 5.0V | 544mA

20181122-152254.985 BATT_INP: Battery Controller Read Error

20181122-152255.088 UA1 | : | 5.0V | 581mA
20181122-152255.191 UA1 | : | 5.0V | 570mA
20181122-152255.294 UA1 | : | 5.0V | 534mA

11.02.2019 | https://www.orn.mpg.de | Copyright 2019 ©, MPIO Seewiesen | page 57

Power Good and Power Fail

- Battery gets disconnected
- Power fail gets detected
- RFID Reader and CAM1 get switched off
- Battery gets reconnected
- normal function without reset, RFID Reader and CAM1 get reactivated on demand

4/18/2017 12:45:06.274 [RX] - 20170418-124506.221 Power-Fail: Received interrupt (POWER FAIL)

4/18/2017 12:51:44.342 [RX] - 20170418-125144.296 LB1:ON

20170418-125144.402 LB2:ON

4/18/2017 12:51:45.030 [RX] - 20170418-125144.985 LB1:off

20170418-125144.986 LB2:off

4/18/2017 12:53:59.514 [RX] - 20170418-125359.436 Power-Fail: Received interrupt (POWER GOOD)

11.02.2019 | https://www.orn.mpg.de | Copyright 2019 ©, MPIO Seewiesen | page 58

## Occurrences when it is not possible to write on the SD card

When the SD card is full or if there is no SD card is in SD card slot an error message is written on the LEUART-BUS. During a normal operation of the Smart Feeder application of the Timed Animal Manipulation Data Logger, it is not common that data is lost due to an absent or malfunctioning SD card, because the internal memory for events provides 2 KB, which should be sufficient for many events to be stored.

ERROR: Log Buffer Out of Memory - lost 1 Messages (only appears on
HyperTerminal screen of the PC)

More error messages:

ERROR Config File - Line 131, pos 26, ID: OUT OF MEMORY

SMB_Reset: Try to recover from invalid state

SMB_Reset: Recovery failed, giving up

CfgRead: FILE OPEN - Error Code

CfgRead: FILE READ - Error Code

CfgRead: Line %d too long

Config File - Line %d, pos %ld: Invalid Variable Name

Config File - Line %d, pos %ld: Unknown Variable

Config File - Line %d, pos %ld: Unknown Variable

Config File - Line %d, pos %ld: Value expected

Config File - Line %d, pos %ld, %s: Invalid time

Config File - Line %d, pos %ld, %s: OUT OF MEMORY

Config File - Line %d, pos %ld, %s: Unsupported data type

Config File - Line %d, pos %ld: Garbage at end of line

LogError ("LogFileOpen: Error Code %d", res);

See if Log File is open */

LogError ("LogFlush: Init Failed");

LogError ("LogFlush: Error Code %d", res);

LogError ("LogFlush: Disk Full");

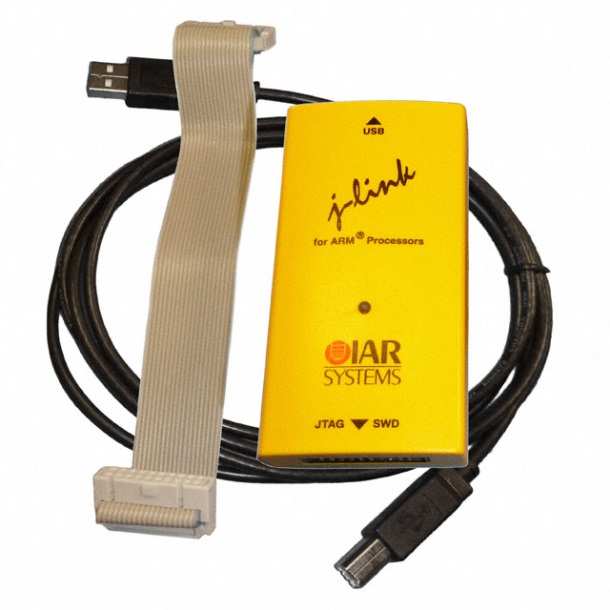
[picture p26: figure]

11.02.2019 | https://www.orn.mpg.de | Copyright 2019 ©, MPIO Seewiesen | page 59

## Procedure after button usage

The Timed Animal Manipulation Data Logger contains a button for conducting a reset.

After pressing the S1 button, the whole system will be restarted. The procedure of the restart is described in chapter Fehler! Verweisquelle konnte nicht gefunden werden..

## Update options

There are three possibilities to write software code on the flash memory.
The method of the Debug Probe and the one via the Debug Interface always work. If software was written on the flash memory via either one of these the methods examining the content of a newly inserted SD card and searching for software updates, a third method can be implemented.

## IAR Systems Debug Probe

Through the debug probe from IAR systems it is possible to load compiled software code on the flash memory. The software from IAR for the debug probe is necessary for this.

IAR Systems also distribute the software IAR Embedded Workbench to create and compile C code. The compiled C code can be loaded on the flash memory by the debug probe.

11.02.2019 | https://www.orn.mpg.de | Copyright 2019 ©, MPIO Seewiesen | page 60

## With USB on 10-pole Debug Interface Connector

This method only allows HEX and BIN files to be transferred to the flash memory and has the benefit of the original C code not being readable anymore.

## Via SD card and boot loader

If software has already been written on the flash memory by either of the methods from chapter 7.2 or 7.3 a third method through a boot loader is available. If the software of the flash memory contains the command to search for new software when recognizing a new SD card, this new software can be installed. (compare 0)

11.02.2019 | https://www.orn.mpg.de | Copyright 2019 ©, MPIO Seewiesen | page 61

## Contact details

address | Max-Planck-Institut für Ornithologie Eberhard-Gwinner-Str. 82319 Seewiesen
web address | http://www.orn.mpg.de/
electronics developer | Dipl. Ing. (FH) Peter Loës
e-mail address | loes@orn.mpg.de
telephone number | Tel: +49 8157 932-330

11.02.2019 | https://www.orn.mpg.de | Copyright 2019 ©, MPIO Seewiesen | page 62

## 8. Links to the datasheets

Datasheets need to be saved within the folder ‘datasheets’, which has to be in the same content as the documentation. For every link there is a document within this folder.

EFM32G230

IAR J Tag ARM

LC display

SD card reader

Button

Capacitor

Lumbergstecker

USB cable

Down converter

LEDS

Radio clock

Light barrier

RFID reader

RFID transponder

Housing for the main board

Housing for the accumulator

Battery charger Fronius

Battery charger Mascot

Battery cell

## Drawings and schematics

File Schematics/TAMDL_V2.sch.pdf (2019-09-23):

# Power Input

# EFM32 Power Regulator

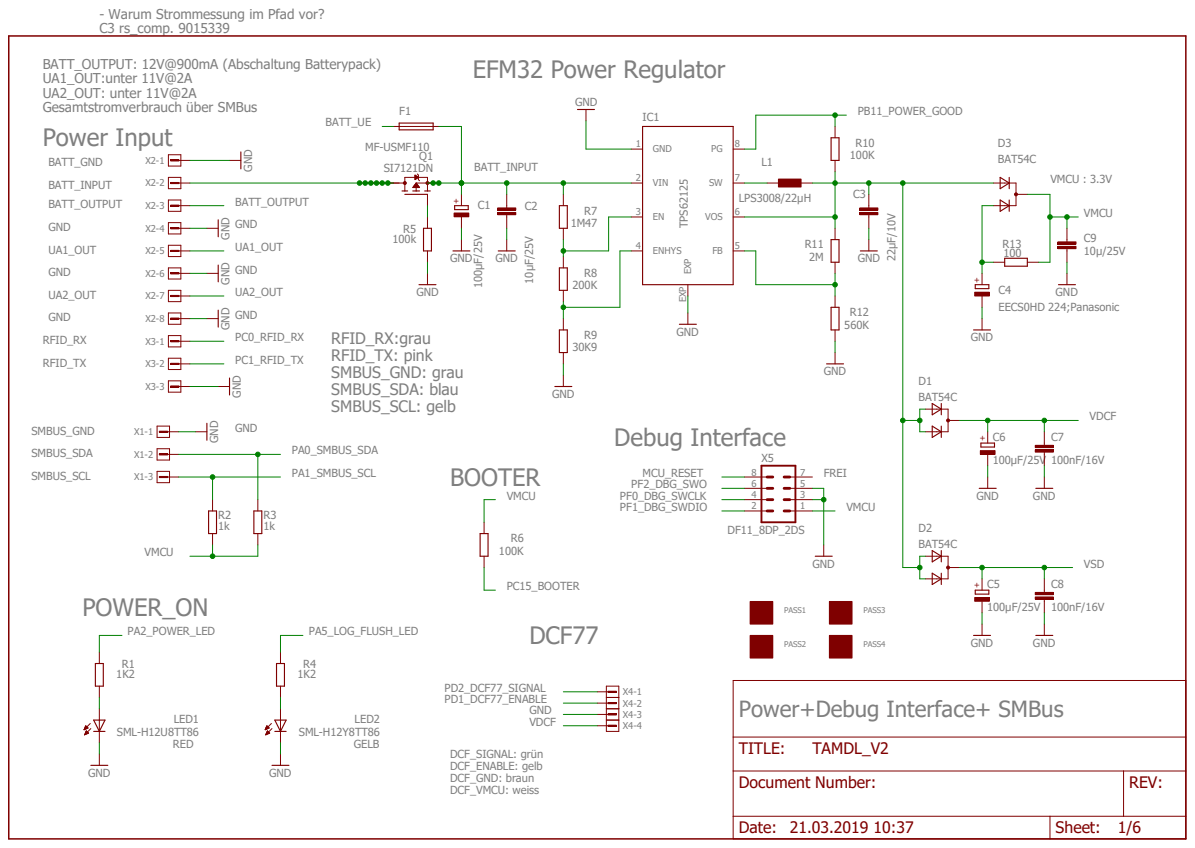
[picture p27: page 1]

- Warum Strommessung im Pfad vor?
C3 rs_comp. 9015339

Power+Debug Interface+ SMBus

Document Number: | REV:

Date: 21.03.2019 10:37 | Sheet: 1/6

EFM32 I/O + POWER | CL f. 32KHz crystal = 22pF as in STK3600

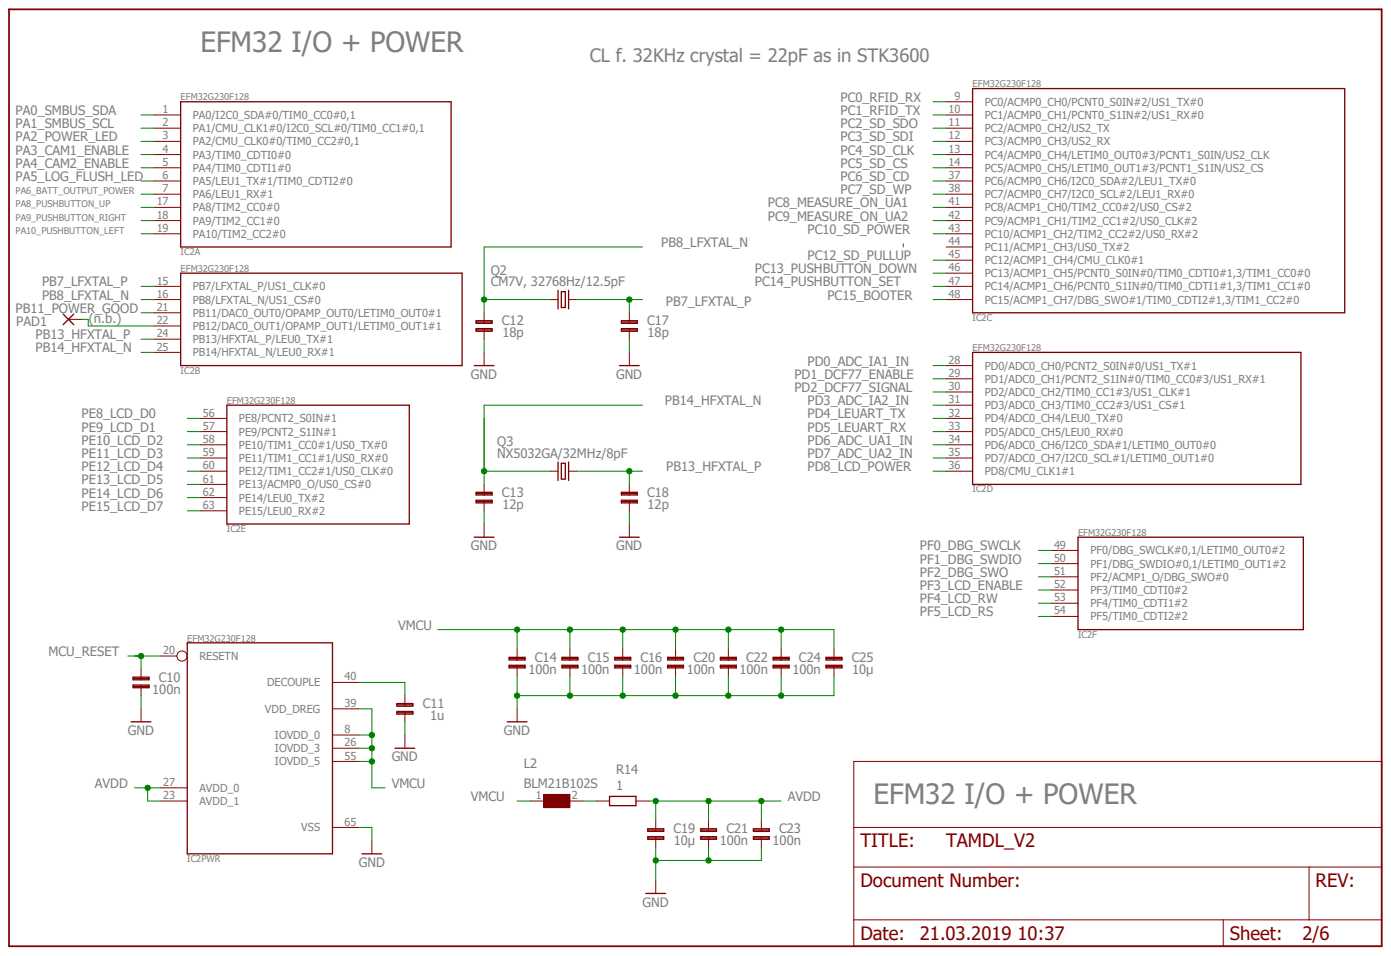
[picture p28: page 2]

Document Number: | REV:

Date: 21.03.2019 10:37 | Sheet: 2/6

# User Pushbutton

# SD Socket

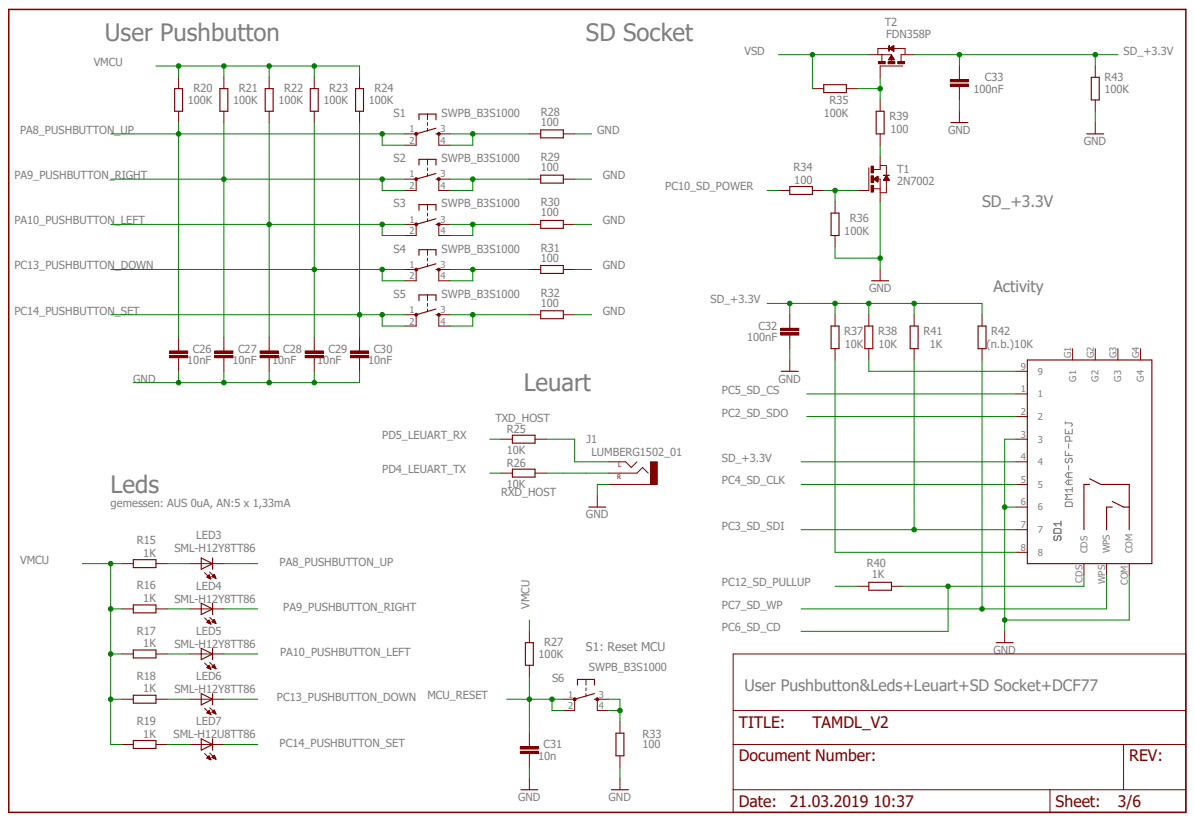
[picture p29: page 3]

User Pushbutton&Leds+Leuart+SD Socket+DCF77

## 9V_Ausgabe

# POWER OUTPUTs

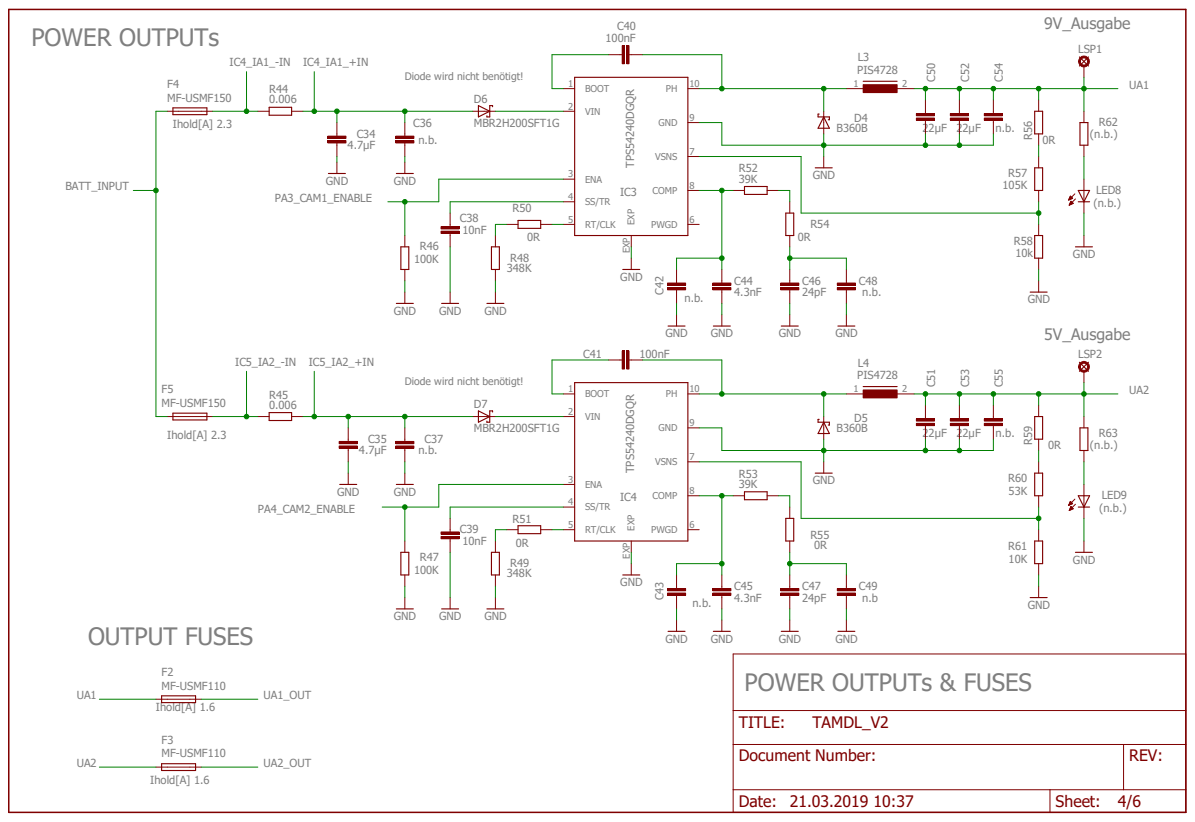
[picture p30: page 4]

Diode wird nicht benötigt!

Document Number: | REV:

Date: 21.03.2019 10:37 | Sheet: 4/6

Output Measurements Current | Output Measurements Voltage

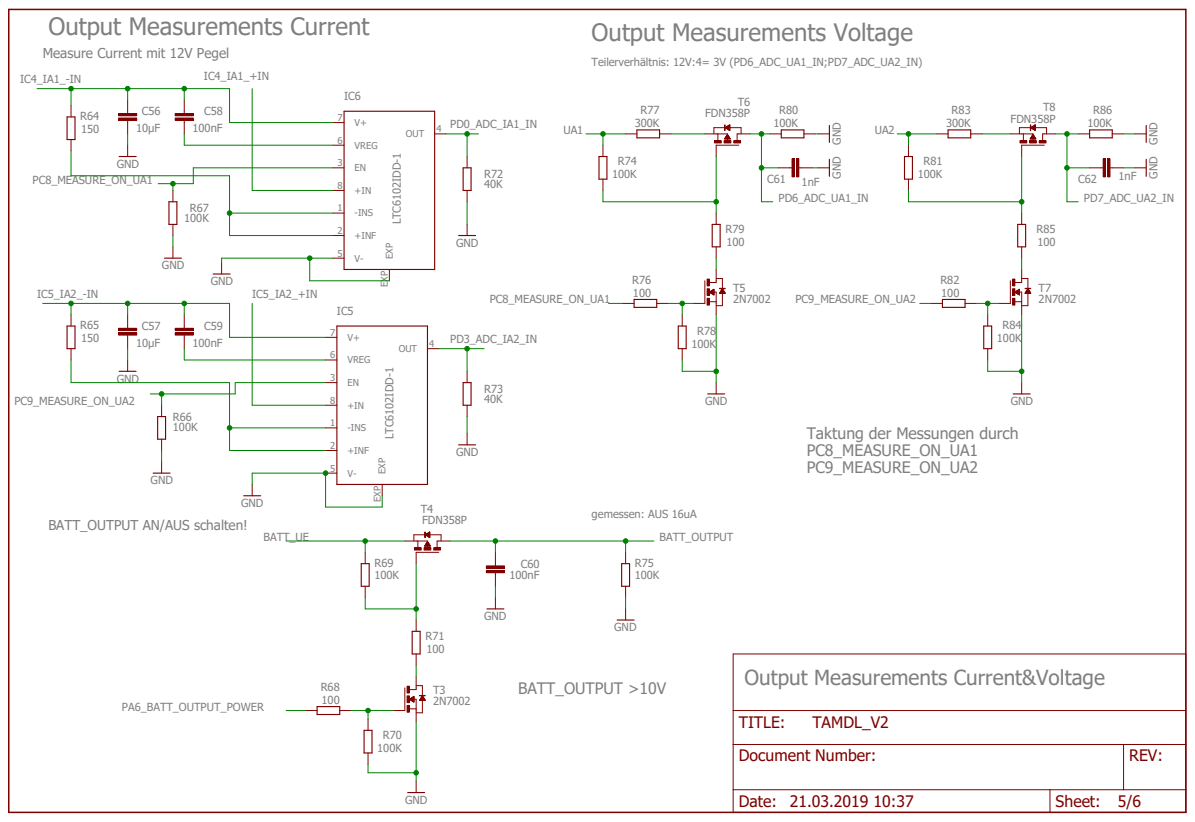
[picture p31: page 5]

Measure Current mit 12V Pegel

Output Measurements Current&Voltage

# LCD ANZEIGE

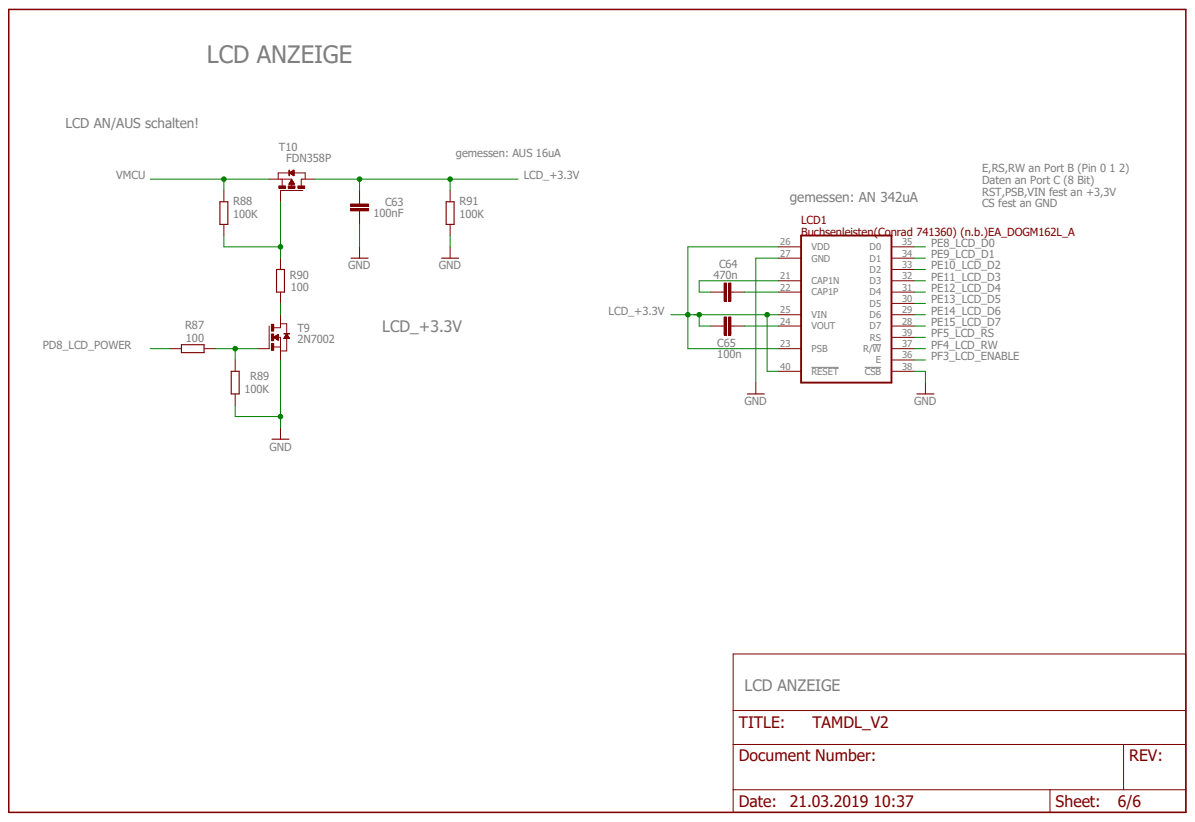
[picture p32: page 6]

LCD AN/AUS schalten!

E,RS,RW an Port B (Pin 0 1 2)
Daten an Port C (8 Bit)
RST,PSB,VIN fest an +3,3V
CS fest an GND

Document Number: | REV:

Date: 21.03.2019 10:37 | Sheet: 6/6

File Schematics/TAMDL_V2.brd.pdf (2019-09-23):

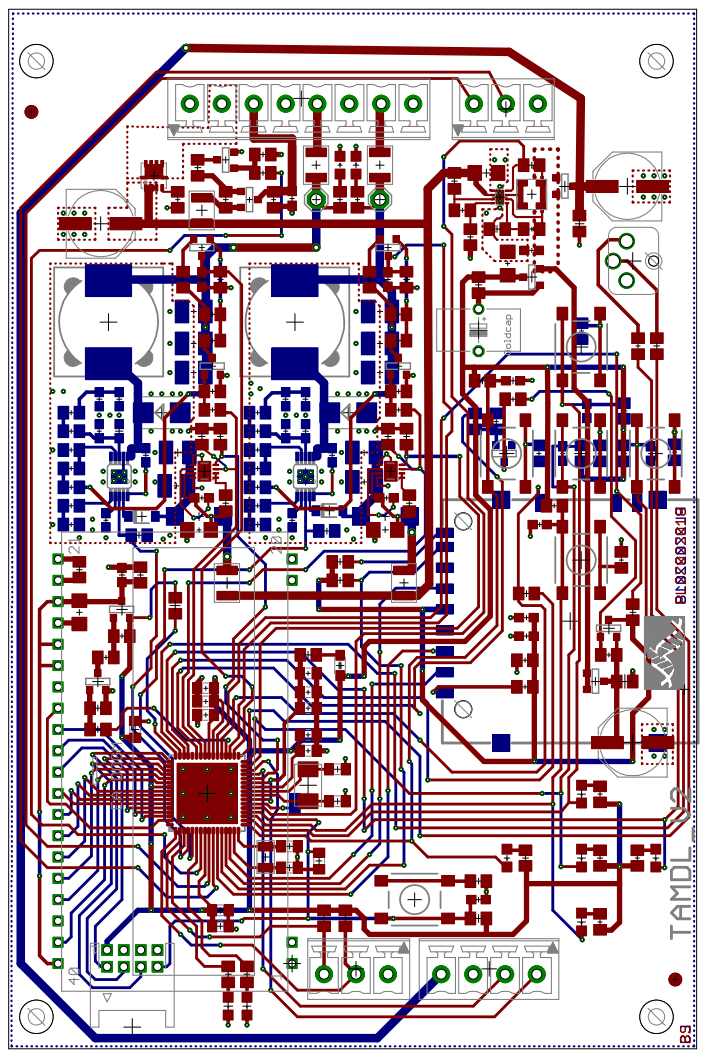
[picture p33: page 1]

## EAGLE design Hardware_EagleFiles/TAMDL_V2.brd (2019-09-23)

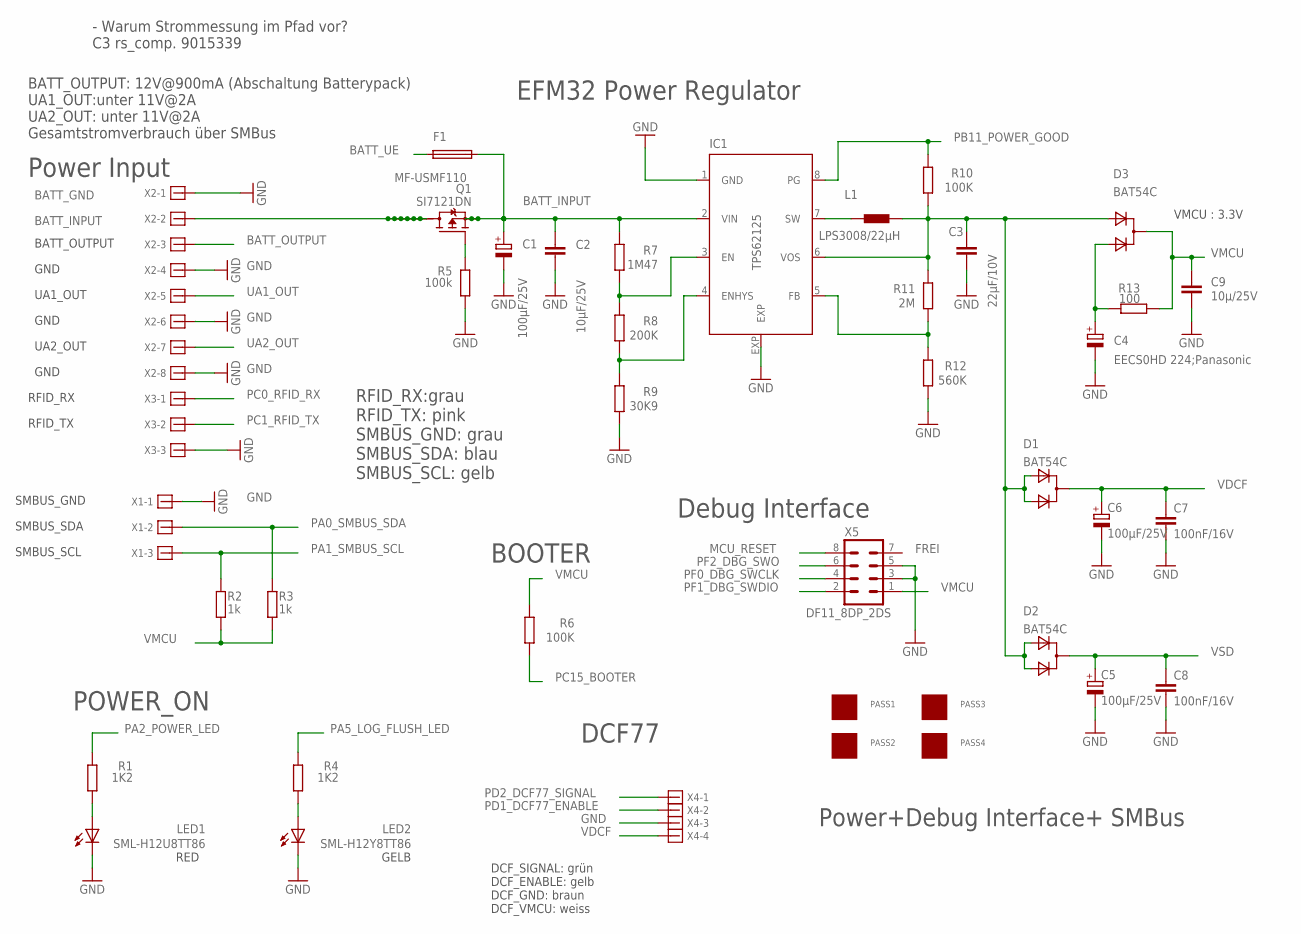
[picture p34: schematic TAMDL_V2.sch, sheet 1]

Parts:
C1, C5, C6: 100µF/25V; PANASONIC_E
C2: 10µF/25V; C1206
C3: 22µF/10V; C0603
C4: EECS0HD 224;Panasonic; GOLDCAPSPK-V
C7, C8: 100nF/16V; C0805
C9: 10µ/25V; C1206
D1, D2, D3: BAT54C; SOT-23$1
F1: MF-USMF110; PFUF_1210POLY
IC1: TPS62125; DSG_PWSO-N8_EXP
L1: LPS3008/22µH; LPS3008
LED1: SML-H12U8TT86; CHIPLED_0805
LED2: SML-H12Y8TT86; CHIPLED_0805
PASS1, PASS2, PASS3, PASS4: ROUND_1MM1.5; ROUND2_1.5MM
Q1: SI7121DN; TRANSISTOR-FET_1212-8S
R1, R4: 1K2; R0805
R2, R3: 1k; R0805
R5: 100k; R0805
R6, R10: 100K; R0805
R7: 1M47; R0805
R8: 200K; R0805
R9: 30K9; R0805
R11: 2M; R0805
R12: 560K; R0805
R13: 100; R0805
X1, X3: 1803439
X2: 1803484
X4: 1803442
X5: DF11_8DP_2DS; DP11_8DP-2DS

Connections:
1: C3.1, D1.2 (A1), D1.3 (A2), D2.2 (A1), D2.3 (A2), D3.2 (A1), IC1.6 (VOS), L1.2, R10.1, R11.2
BAT+: Q1.5 (D), Q1.6 (D), Q1.7 (D), Q1.8 (D), Q1.9 (D), Q1.10 (D), Q1.11 (D), X2.2
BATT_INPUT: C1.+, C2.1, F1.P$2 (2), IC1.2 (VIN), Q1.1 (S), Q1.2 (S), Q1.3 (S), R7.2; also elsewhere on the board
BATT_OUTPUT: X2.3; also elsewhere on the board
BATT_UE: F1.P$1 (1); also elsewhere on the board
GND: C1.-, C2.2, C3.2, C4.-, C5.-, C6.-, C7.2, C8.2, C9.1, IC1.1 (GND), IC1.EXP, LED1.C, LED2.C, R5.1, R9.1, R12.1, X1.1, X2.1, X2.4, X2.6, X2.8, X3.3, X4.3, X5.3, X5.5; also elsewhere on the board
MCU_RESET: X5.8; also elsewhere on the board
unnamed: LED1.A, R1.2
unnamed: C4.+, D3.3 (A2), R13.2
unnamed: LED2.A, R4.2
unnamed: IC1.3 (EN), R7.1, R8.2
unnamed: IC1.4 (ENHYS), R8.1, R9.2
unnamed: IC1.7 (SW), L1.1
unnamed: IC1.5 (FB), R11.1, R12.2
unnamed: Q1.4 (G), R5.2
PA0_SMBUS_SDA: R3.2, X1.2; also elsewhere on the board
PA1_SMBUS_SCL: R2.2, X1.3; also elsewhere on the board
PA2_POWER_LED: R1.1; also elsewhere on the board
PA5_LOG_FLUSH_LED: R4.1; also elsewhere on the board
PB11_POWER_GOOD: IC1.8 (PG), R10.2; also elsewhere on the board
PC0_RFID_RX: X3.1; also elsewhere on the board
PC1_RFID_TX: X3.2; also elsewhere on the board
PC15_BOOTER: R6.1; also elsewhere on the board
PD1_DCF77_ENABLE: X4.2; also elsewhere on the board
PD2_DCF77_SIGNAL: X4.1; also elsewhere on the board
PF0_DBG_SWCLK: X5.4; also elsewhere on the board
PF1_DBG_SWDIO: X5.2; also elsewhere on the board
PF2_DBG_SWO: X5.6; also elsewhere on the board
UA1_OUT: X2.5; also elsewhere on the board
UA2_OUT: X2.7; also elsewhere on the board
VDCF: C6.+, C7.1, D1.1 (C), X4.4
VMCU: C9.2, D3.1 (C), R2.1, R3.1, R6.2, R13.1, X5.1; also elsewhere on the board
VSD: C5.+, C8.1, D2.1 (C); also elsewhere on the board

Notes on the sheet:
BATT_GND
BATT_INPUT
BATT_OUTPUT
UA1_OUT
UA2_OUT
GND
RFID_RX
Power+Debug Interface+ SMBus
Power Input
SMBUS_SCL
SMBUS_SDA
SMBUS_GND
EFM32 Power Regulator
Debug Interface
POWER_ON
FREI
VMCU : 3.3V
RED
GELB
BATT_OUTPUT: 12V@900mA (Abschaltung Batterypack) UA1_OUT:unter 11V@2A UA2_OUT: unter 11V@2A Gesamtstromverbrauch über SMBus
RFID_TX
DCF77
RFID_RX:grau RFID_TX: pink SMBUS_GND: grau SMBUS_SDA: blau SMBUS_SCL: gelb
DCF_SIGNAL: grün DCF_ENABLE: gelb DCF_GND: braun DCF_VMCU: weiss
- Warum Strommessung im Pfad vor? C3 rs_comp. 9015339
BOOTER

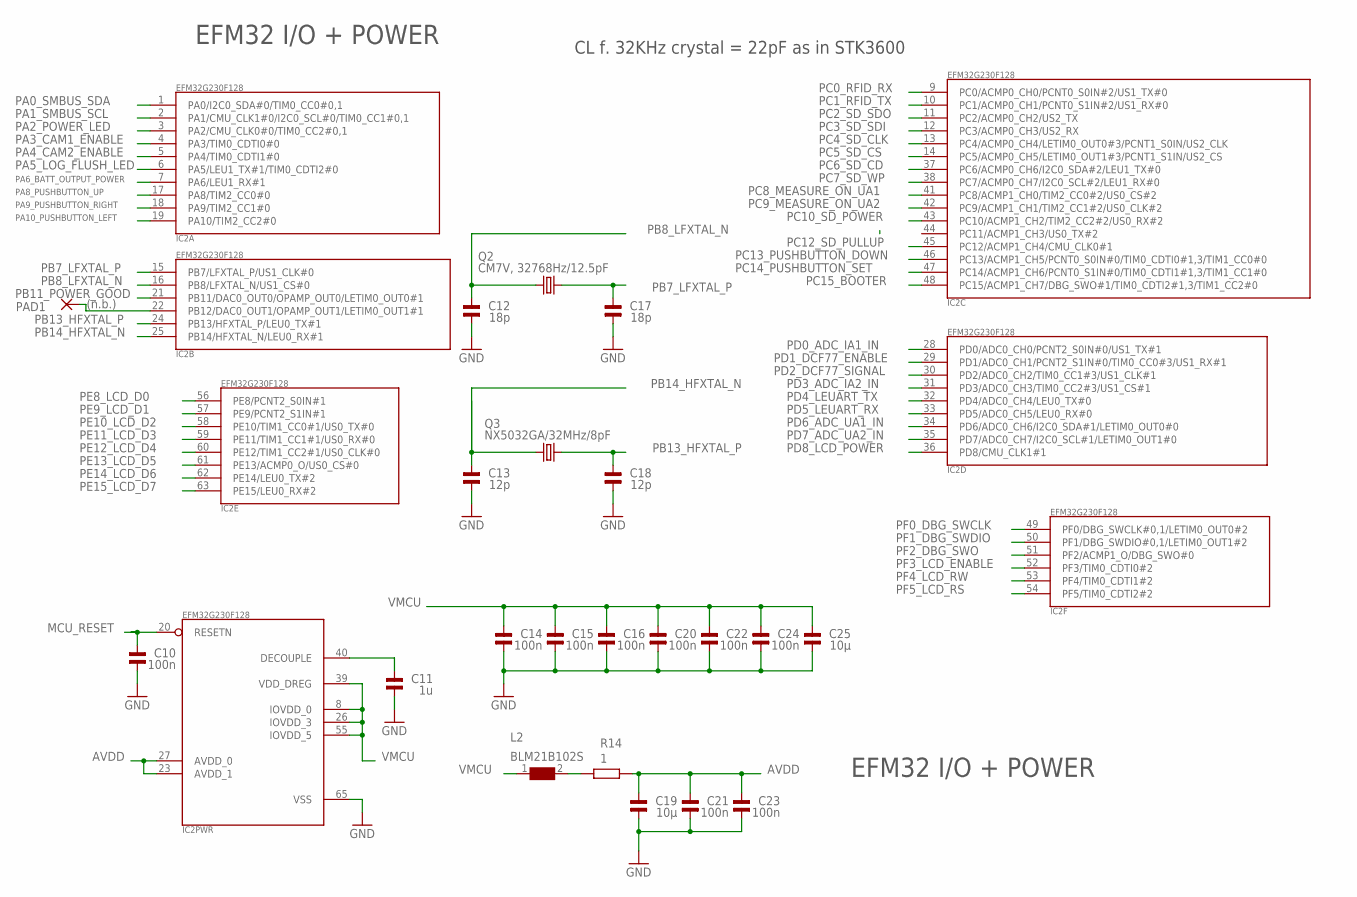
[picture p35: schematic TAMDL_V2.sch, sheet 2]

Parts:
C10, C14, C15, C16, C20, C21, C22, C23, C24: 100n; 0805
C11: 1u; 0805
C12, C17: 18p; 0805
C13, C18: 12p; 0805
C19, C25: 10µ; 0805
IC2: EFM32G230F128; QFN64
L2: BLM21B102S; 0805
PAD1: (n.b.); SMD1,27-2,54
Q2: CM7V, 32768Hz/12.5pF; CRYSTAL2P3.2X1.5
Q3: NX5032GA/32MHz/8pF; CRYSTAL2P5.0X3.2
R14: 1; R0805

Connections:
AVDD: C19.2, C21.2, C23.2, IC2.23 (AVDD_1), IC2.27 (AVDD_0), R14.2
GND: C10.1, C11.1, C12.1, C13.1, C14.1, C15.1, C16.1, C17.1, C18.1, C19.1, C20.1, C21.1, C22.1, C23.1, C24.1, C25.1, IC2.65 (VSS); also elsewhere on the board
MCU_RESET: C10.2, IC2.20 (RESETN); also elsewhere on the board
unnamed: L2.2, R14.1
unnamed: IC2.22 (PB12/DAC0_OUT1/OPAMP_OUT1/LETIM0_OUT1#1), PAD1.1
unnamed: C11.2, IC2.40 (DECOUPLE)
PA0_SMBUS_SDA: IC2.1 (PA0/I2C0_SDA#0/TIM0_CC0#0,1); also elsewhere on the board
PA1_SMBUS_SCL: IC2.2 (PA1/CMU_CLK1#0/I2C0_SCL#0/TIM0_CC1#0,1); also elsewhere on the board
PA2_POWER_LED: IC2.3 (PA2/CMU_CLK0#0/TIM0_CC2#0,1); also elsewhere on the board
PA3_CAM1_ENABLE: IC2.4 (PA3/TIM0_CDTI0#0); also elsewhere on the board
PA4_CAM2_ENABLE: IC2.5 (PA4/TIM0_CDTI1#0); also elsewhere on the board
PA5_LOG_FLUSH_LED: IC2.6 (PA5/LEU1_TX#1/TIM0_CDTI2#0); also elsewhere on the board
PA6_BATT_OUTPUT_POWER: IC2.7 (PA6/LEU1_RX#1); also elsewhere on the board
PA8_PUSHBUTTON_UP: IC2.17 (PA8/TIM2_CC0#0); also elsewhere on the board
PA9_PUSHBUTTON_RIGHT: IC2.18 (PA9/TIM2_CC1#0); also elsewhere on the board
PA10_PUSHBUTTON_LEFT: IC2.19 (PA10/TIM2_CC2#0); also elsewhere on the board
PB7_LFXTAL_P: C17.2, IC2.15 (PB7/LFXTAL_P/US1_CLK#0), Q2.2
PB8_LFXTAL_N: C12.2, IC2.16 (PB8/LFXTAL_N/US1_CS#0), Q2.1
PB11_POWER_GOOD: IC2.21 (PB11/DAC0_OUT0/OPAMP_OUT0/LETIM0_OUT0#1); also elsewhere on the board
PB13_HFXTAL_P: C18.2, IC2.24 (PB13/HFXTAL_P/LEU0_TX#1), Q3.2
PB14_HFXTAL_N: C13.2, IC2.25 (PB14/HFXTAL_N/LEU0_RX#1), Q3.1
PC0_RFID_RX: IC2.9 (PC0/ACMP0_CH0/PCNT0_S0IN#2/US1_TX#0); also elsewhere on the board
PC1_RFID_TX: IC2.10 (PC1/ACMP0_CH1/PCNT0_S1IN#2/US1_RX#0); also elsewhere on the board
PC2_SD_SDO: IC2.11 (PC2/ACMP0_CH2/US2_TX); also elsewhere on the board
PC3_SD_SDI: IC2.12 (PC3/ACMP0_CH3/US2_RX); also elsewhere on the board
PC4_SD_CLK: IC2.13 (PC4/ACMP0_CH4/LETIM0_OUT0#3/PCNT1_S0IN/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); also elsewhere on the board
PC5_SD_CS: IC2.14 (PC5/ACMP0_CH5/LETIM0_OUT1#3/PCNT1_S1IN/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); also elsewhere on the board
PC6_SD_CD: IC2.37 (PC6/ACMP0_CH6/I2C0_SDA#2/LEU1_TX#0); also elsewhere on the board
PC7_SD_WP: IC2.38 (PC7/ACMP0_CH7/I2C0_SCL#2/LEU1_RX#0); also elsewhere on the board
PC8_MEASURE_ON_UA1: IC2.41 (PC8/ACMP1_CH0/TIM2_CC0#2/US0_CS#2); also elsewhere on the board
PC9_MEASURE_ON_UA2: IC2.42 (PC9/ACMP1_CH1/TIM2_CC1#2/US0_CLK#2); also elsewhere on the board
PC10_SD_POWER: IC2.43 (PC10/ACMP1_CH2/TIM2_CC2#2/US0_RX#2); also elsewhere on the board
PC12_SD_PULLUP: IC2.45 (PC12/ACMP1_CH4/CMU_CLK0#1); also elsewhere on the board
PC13_PUSHBUTTON_DOWN: IC2.46 (PC13/ACMP1_CH5/PCNT0_S0IN#0/TIM0_CDTI0#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); also elsewhere on the board
PC14_PUSHBUTTON_SET: IC2.47 (PC14/ACMP1_CH6/PCNT0_S1IN#0/TIM0_CDTI1#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); also elsewhere on the board
PC15_BOOTER: IC2.48 (PC15/ACMP1_CH7/DBG_SWO#1/TIM0_CDTI2#1,3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); also elsewhere on the board
PD0_ADC_IA1_IN: IC2.28 (PD0/ADC0_CH0/PCNT2_S0IN#0/US1_TX#1); also elsewhere on the board
PD1_DCF77_ENABLE: IC2.29 (PD1/ADC0_CH1/PCNT2_S1IN#0/TIM0_CC0#3/US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); also elsewhere on the board
PD2_DCF77_SIGNAL: IC2.30 (PD2/ADC0_CH2/TIM0_CC1#3/US1_CLK#1); also elsewhere on the board
PD3_ADC_IA2_IN: IC2.31 (PD3/ADC0_CH3/TIM0_CC2#3/US1_CS#1); also elsewhere on the board
PD4_LEUART_TX: IC2.32 (PD4/ADC0_CH4/LEU0_TX#0); also elsewhere on the board
PD5_LEUART_RX: IC2.33 (PD5/ADC0_CH5/LEU0_RX#0); also elsewhere on the board
PD6_ADC_UA1_IN: IC2.34 (PD6/ADC0_CH6/I2C0_SDA#1/LETIM0_OUT0#0); also elsewhere on the board
PD7_ADC_UA2_IN: IC2.35 (PD7/ADC0_CH7/I2C0_SCL#1/LETIM0_OUT1#0); also elsewhere on the board
PD8_LCD_POWER: IC2.36 (PD8/CMU_CLK1#1); also elsewhere on the board
PE8_LCD_D0: IC2.56 (PE8/PCNT2_S0IN#1); also elsewhere on the board
PE9_LCD_D1: IC2.57 (PE9/PCNT2_S1IN#1); also elsewhere on the board
PE10_LCD_D2: IC2.58 (PE10/TIM1_CC0#1/US0_TX#0); also elsewhere on the board
PE11_LCD_D3: IC2.59 (PE11/TIM1_CC1#1/US0_RX#0); also elsewhere on the board
PE12_LCD_D4: IC2.60 (PE12/TIM1_CC2#1/US0_CLK#0); also elsewhere on the board
PE13_LCD_D5: IC2.61 (PE13/ACMP0_O/US0_CS#0); also elsewhere on the board
PE14_LCD_D6: IC2.62 (PE14/LEU0_TX#2); also elsewhere on the board
PE15_LCD_D7: IC2.63 (PE15/LEU0_RX#2); also elsewhere on the board
PF0_DBG_SWCLK: IC2.49 (PF0/DBG_SWCLK#0,1/LETIM0_OUT0#2); also elsewhere on the board
PF1_DBG_SWDIO: IC2.50 (PF1/DBG_SWDIO#0,1/LETIM0_OUT1#2); also elsewhere on the board
PF2_DBG_SWO: IC2.51 (PF2/ACMP1_O/DBG_SWO#0); also elsewhere on the board
PF3_LCD_ENABLE: IC2.52 (PF3/TIM0_CDTI0#2); also elsewhere on the board
PF4_LCD_RW: IC2.53 (PF4/TIM0_CDTI1#2); also elsewhere on the board
PF5_LCD_RS: IC2.54 (PF5/TIM0_CDTI2#2); also elsewhere on the board
VMCU: C14.2, C15.2, C16.2, C20.2, C22.2, C24.2, C25.2, IC2.8 (IOVDD_0), IC2.26 (IOVDD_3), IC2.39 (VDD_DREG), IC2.55 (IOVDD_5), L2.1; also elsewhere on the board

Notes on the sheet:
EFM32 I/O + POWER
CL f. 32KHz crystal = 22pF as in STK3600

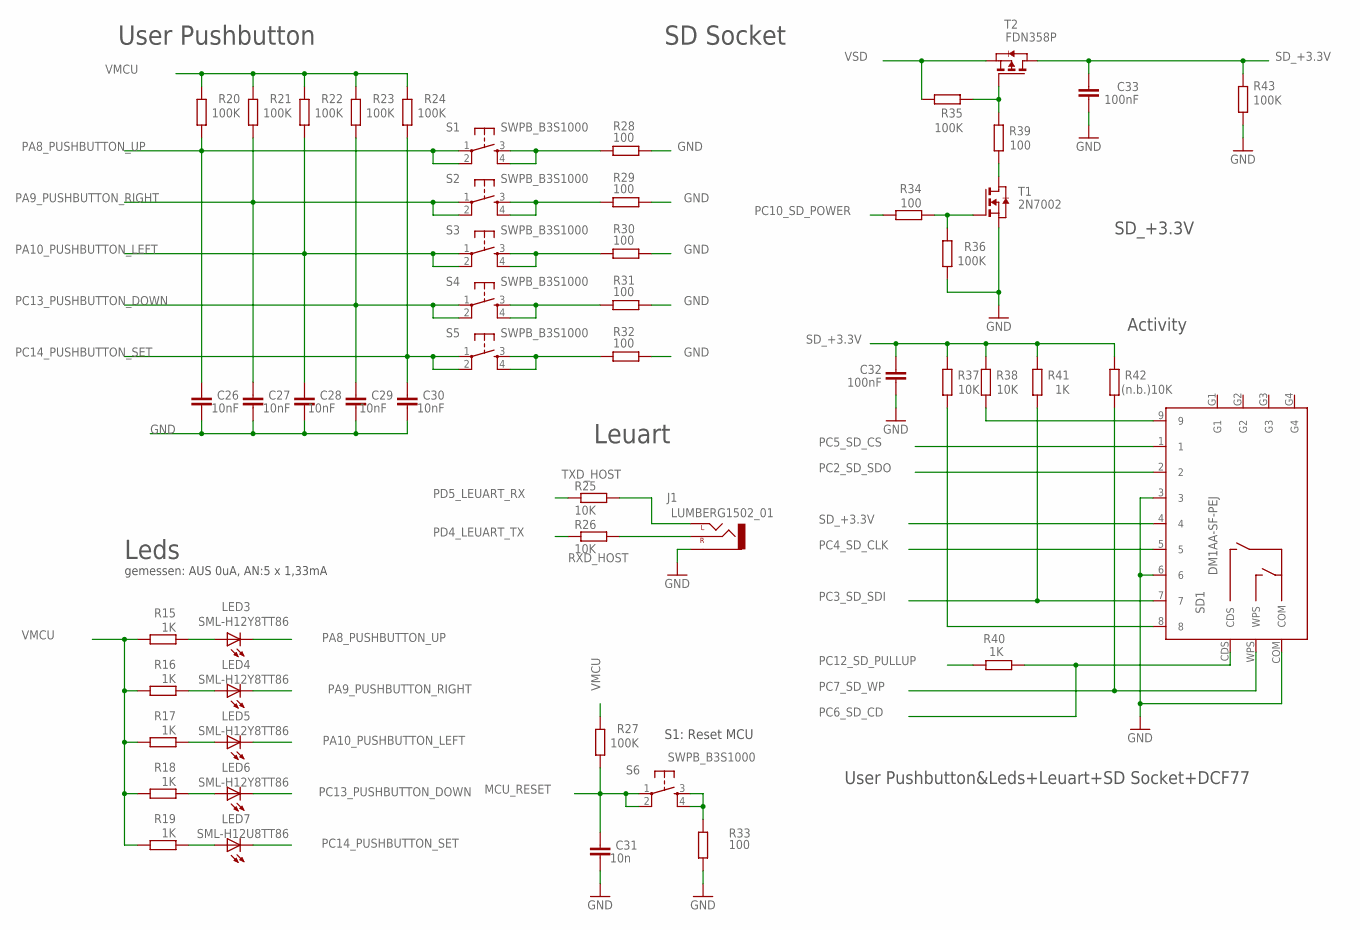
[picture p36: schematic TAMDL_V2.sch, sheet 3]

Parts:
C26, C27, C28, C29, C30: 10nF; C0603
C31: 10n; C0603
C32, C33: 100nF; C0603
J1: LUMBERG1502_01
LED3, LED4, LED5, LED6: SML-H12Y8TT86; CHIPLED_0805
LED7: SML-H12U8TT86; CHIPLED_0805
R15, R16, R17, R18, R19, R40, R41: 1K; R0805
R20, R21, R22, R23, R24, R27, R35, R36, R43: 100K; R0805
R25, R26, R37, R38: 10K; R0805
R28, R29, R30, R31, R32, R33, R34, R39: 100; R0805
R42: (n.b.)10K; R0805
S1, S2, S3, S4, S5, S6: SWPB_B3S1000; DTSM-6
SD1: DM1AA-SF-PEJ
T1: 2N7002; ZETEX_SOT-23
T2: FDN358P; ZETEX_SOT-23

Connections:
GND: C26.1, C27.1, C28.1, C29.1, C30.1, C31.1, C32.2, C33.2, J1.P$1 (1-SLEEVE), R28.2, R29.2, R30.2, R31.2, R32.2, R33.2, R36.1, R43.1, SD1.3, SD1.6, SD1.COM, T1.2 (S); also elsewhere on the board
MCU_RESET: C31.2, R27.1, S6.1, S6.2; also elsewhere on the board
unnamed: R33.1, S6.3, S6.4
unnamed: R38.1, SD1.9
unnamed: R37.1, SD1.8
unnamed: LED3.A, R15.1
unnamed: R28.1, S1.3, S1.4
unnamed: R29.1, S2.3, S2.4
unnamed: R30.1, S3.3, S3.4
unnamed: R31.1, S4.3, S4.4
unnamed: R32.1, S5.3, S5.4
unnamed: LED4.A, R16.1
unnamed: R35.1, R39.2, T2.3 (G)
unnamed: R39.1, T1.1 (D)
unnamed: R34.1, R36.2, T1.3 (G)
unnamed: LED5.A, R17.1
unnamed: LED6.A, R18.1
unnamed: LED7.A, R19.1
PA8_PUSHBUTTON_UP: C26.2, LED3.C, R20.1, S1.1, S1.2; also elsewhere on the board
PA9_PUSHBUTTON_RIGHT: C27.2, LED4.C, R21.1, S2.1, S2.2; also elsewhere on the board
PA10_PUSHBUTTON_LEFT: C28.2, LED5.C, R22.1, S3.1, S3.2; also elsewhere on the board
PC2_SD_SDO: SD1.2; also elsewhere on the board
PC3_SD_SDI: R41.1, SD1.7; also elsewhere on the board
PC4_SD_CLK: SD1.5; also elsewhere on the board
PC5_SD_CS: SD1.1; also elsewhere on the board
PC6_SD_CD: R40.2, SD1.CDS; also elsewhere on the board
PC7_SD_WP: R42.1, SD1.WPS; also elsewhere on the board
PC10_SD_POWER: R34.2; also elsewhere on the board
PC12_SD_PULLUP: R40.1; also elsewhere on the board
PC13_PUSHBUTTON_DOWN: C29.2, LED6.C, R23.1, S4.1, S4.2; also elsewhere on the board
PC14_PUSHBUTTON_SET: C30.2, LED7.C, R24.1, S5.1, S5.2; also elsewhere on the board
PD4_LEUART_TX: R26.1; also elsewhere on the board
PD5_LEUART_RX: R25.1; also elsewhere on the board
RXD_HOST: J1.P$3 (3-RIGHT), R26.2
SD_+3.3V: C32.1, C33.1, R37.2, R38.2, R41.2, R42.2, R43.2, SD1.4, T2.1 (D)
TXD_HOST: J1.P$2 (2-LEFT), R25.2
VMCU: R15.2, R16.2, R17.2, R18.2, R19.2, R20.2, R21.2, R22.2, R23.2, R24.2, R27.2; also elsewhere on the board
VSD: R35.2, T2.2 (S); also elsewhere on the board

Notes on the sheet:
gemessen: AUS 0uA, AN:5 x 1,33mA
User Pushbutton&Leds+Leuart+SD Socket+DCF77
User Pushbutton
Leds
Leuart
SD Socket
SD_+3.3V
Activity
S1: Reset MCU

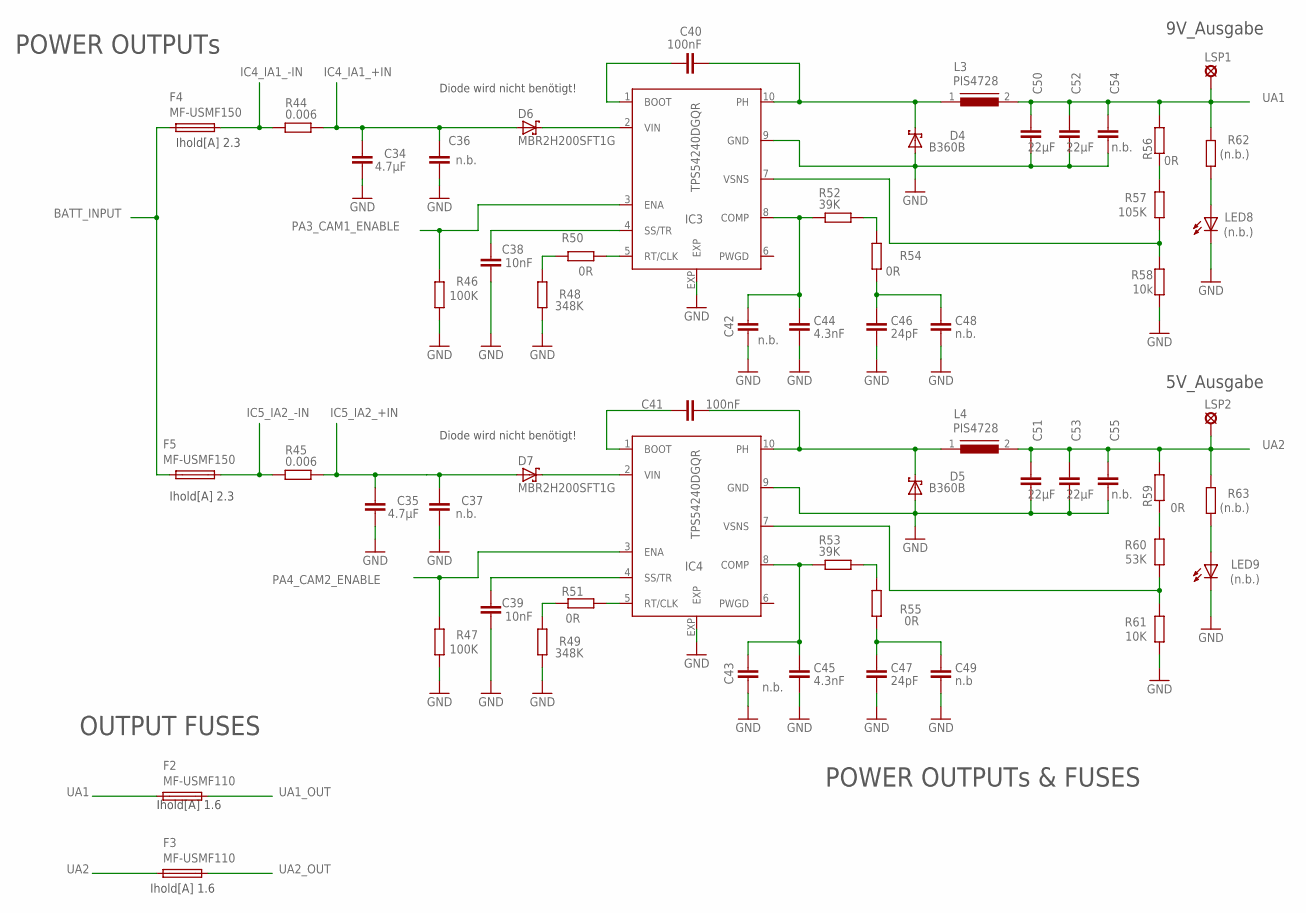
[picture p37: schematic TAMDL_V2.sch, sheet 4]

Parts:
C34, C35: 4.7µF; C1210
C36, C37, C54, C55: n.b.; C1210
C38, C39: 10nF; C0603
C40, C41: 100nF; C0603
C42, C43, C48: n.b.; C0603
C44, C45: 4.3nF; C0603
C46, C47: 24pF; C0603
C49: n.b; C0603
C50, C51, C52, C53: 22µF; C1210
D4, D5: B360B; SMB
D6, D7: MBR2H200SFT1G; SOD123FL
F2, F3: MF-USMF110; PFUF_1210POLY
F4, F5: MF-USMF150; PFUF_1210POLY
IC3, IC4: TPS54240DGQR; S-PDSO-G10
L3, L4: PIS4728; DR127
LED8, LED9: (n.b.); CHIPLED_0805
LSP1, LSP2: (n.b.)SE13; SE13
R44, R45: 0.006; R2512W
R46, R47: 100K; R0805
R48, R49: 348K; R0805
R50, R51, R54, R55, R56, R59: 0R; R0805
R52, R53: 39K; R0805
R57: 105K; R0805
R58: 10k; R0805
R60: 53K; R0805
R61: 10K; R0805
R62, R63: (n.b.); R0805

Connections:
BATT_INPUT: F4.P$1 (1), F5.P$1 (1); also elsewhere on the board
GND: C34.2, C35.2, C36.2, C37.2, C38.2, C39.2, C42.2, C43.2, C44.2, C45.2, C46.2, C47.2, C48.2, C49.2, C50.2, C51.2, C52.2, C53.2, C54.2, C55.2, D4.A, D5.A, IC3.9 (GND), IC3.EXP, IC4.9 (GND), IC4.EXP, LED8.C, LED9.C, R46.1, R47.1, R48.1, R49.1, R58.1, R61.1; also elsewhere on the board
IC4_IA1_+IN: C34.1, C36.1, D6.A, R44.2; also elsewhere on the board
IC4_IA1_-IN: F4.P$2 (2), R44.1; also elsewhere on the board
IC5_IA2_+IN: C35.1, C37.1, D7.A, R45.2; also elsewhere on the board
IC5_IA2_-IN: F5.P$2 (2), R45.1; also elsewhere on the board
unnamed: C40.2, IC3.1 (BOOT)
unnamed: C40.1, D4.C, IC3.10 (PH), L3.1
unnamed: C38.1, IC3.4 (SS/TR)
unnamed: C42.1, C44.1, IC3.8 (COMP), R52.1
unnamed: C46.1, C48.1, R54.1
unnamed: IC3.7 (VSNS), R57.1, R58.2
unnamed: C41.2, IC4.1 (BOOT)
unnamed: C41.1, D5.C, IC4.10 (PH), L4.1
unnamed: C39.1, IC4.4 (SS/TR)
unnamed: C43.1, C45.1, IC4.8 (COMP), R53.1
unnamed: C47.1, C49.1, R55.1
unnamed: IC4.7 (VSNS), R60.1, R61.2
unnamed: LED9.A, R63.1
unnamed: R48.2, R50.1
unnamed: D6.C, IC3.2 (VIN)
unnamed: R49.2, R51.1
unnamed: IC3.5 (RT/CLK), R50.2
unnamed: R52.2, R54.2
unnamed: R56.1, R57.2
unnamed: IC4.5 (RT/CLK), R51.2
unnamed: R59.1, R60.2
unnamed: R53.2, R55.2
unnamed: D7.C, IC4.2 (VIN)
unnamed: LED8.A, R62.1
PA3_CAM1_ENABLE: IC3.3 (ENA), R46.2; also elsewhere on the board
PA4_CAM2_ENABLE: IC4.3 (ENA), R47.2; also elsewhere on the board
UA1: C50.1, C52.1, C54.1, F2.P$1 (1), L3.2, LSP1.MP, R56.2, R62.2; also elsewhere on the board
UA1_OUT: F2.P$2 (2); also elsewhere on the board
UA2: C51.1, C53.1, C55.1, F3.P$1 (1), L4.2, LSP2.MP, R59.2, R63.2; also elsewhere on the board
UA2_OUT: F3.P$2 (2); also elsewhere on the board

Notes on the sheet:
9V_Ausgabe
5V_Ausgabe
POWER OUTPUTs & FUSES
POWER OUTPUTs
OUTPUT FUSES
Ihold[A] 2.3
Ihold[A] 1.6
Diode wird nicht benötigt!

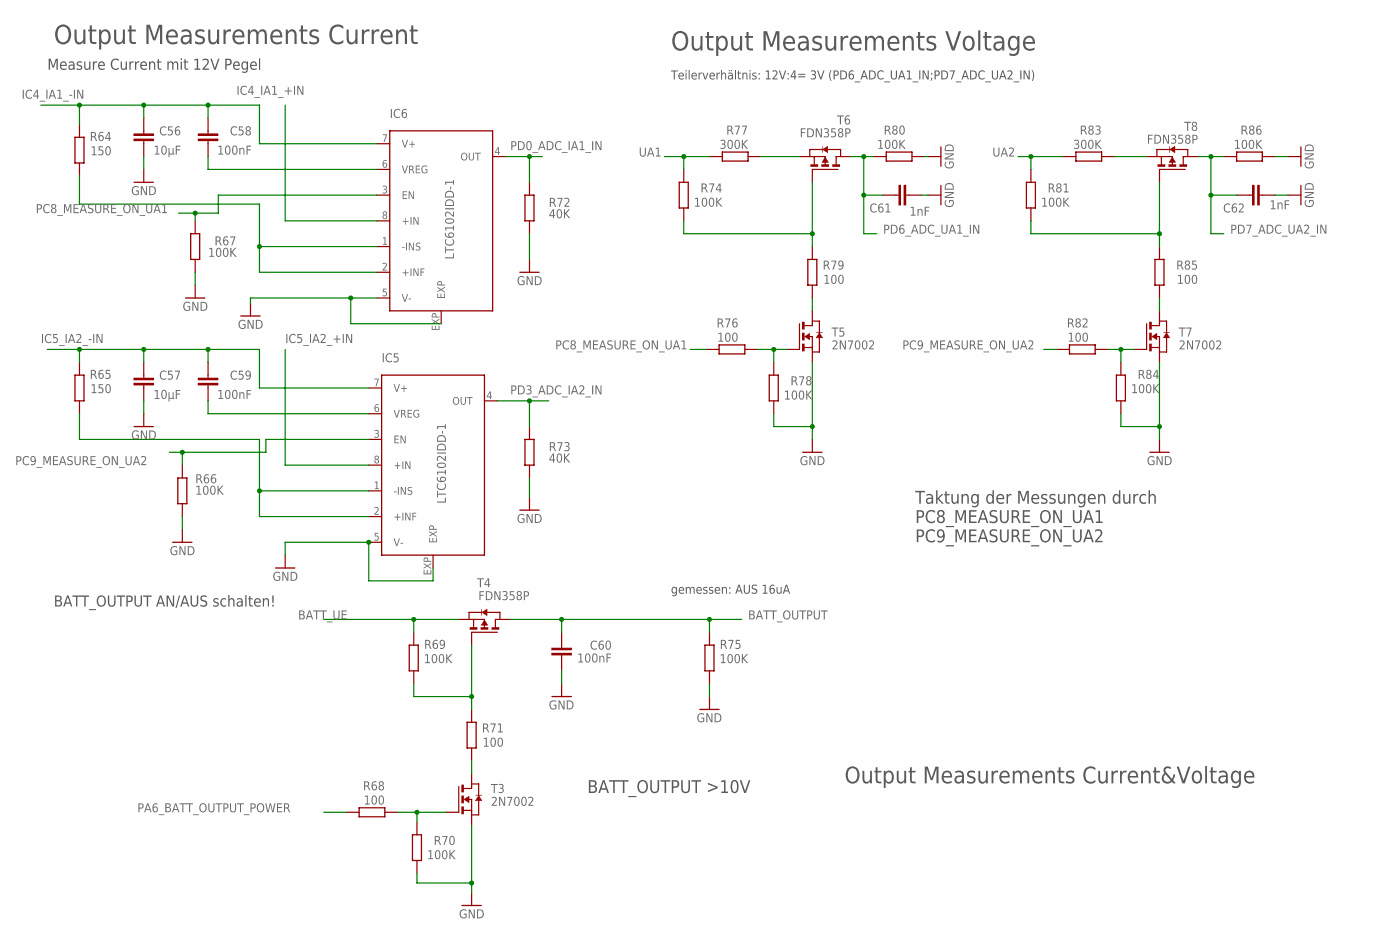
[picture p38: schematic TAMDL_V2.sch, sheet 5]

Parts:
C56, C57: 10µF; C1206
C58, C59, C60: 100nF; C0603
C61, C62: 1nF; C0603
IC5, IC6: LTC6102IDD-1; DFN8-LEAD
R64, R65: 150; R0805
R66, R67, R69, R70, R74, R75, R78, R80, R81, R84, R86: 100K; R0805
R68, R71, R76, R79, R82, R85: 100; R0805
R72, R73: 40K; R0805
R77, R83: 300K; R0805
T3, T5, T7: 2N7002; ZETEX_SOT-23
T4, T6, T8: FDN358P; ZETEX_SOT-23

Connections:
BATT_OUTPUT: C60.1, R75.2, T4.1 (D); also elsewhere on the board
BATT_UE: R69.2, T4.2 (S); also elsewhere on the board
GND: C56.1, C57.1, C60.2, C61.2, C62.2, IC5.5 (V-), IC5.EXP, IC6.5 (V-), IC6.EXP, R66.2, R67.2, R70.1, R72.2, R73.2, R75.1, R78.1, R80.1, R84.1, R86.1, T3.2 (S), T5.2 (S), T7.2 (S); also elsewhere on the board
IC4_IA1_+IN: IC6.8 (+IN); also elsewhere on the board
IC4_IA1_-IN: C56.2, C58.2, IC6.7 (V+), R64.2; also elsewhere on the board
IC5_IA2_+IN: IC5.8 (+IN); also elsewhere on the board
IC5_IA2_-IN: C57.2, C59.2, IC5.7 (V+), R65.2; also elsewhere on the board
unnamed: R69.1, R71.2, T4.3 (G)
unnamed: R71.1, T3.1 (D)
unnamed: R68.1, R70.2, T3.3 (G)
unnamed: R74.1, R79.2, T6.3 (G)
unnamed: IC6.1 (-INS), IC6.2 (+INF), R64.1
unnamed: C58.1, IC6.6 (VREG)
unnamed: IC5.1 (-INS), IC5.2 (+INF), R65.1
unnamed: C59.1, IC5.6 (VREG)
unnamed: R79.1, T5.1 (D)
unnamed: R76.1, R78.2, T5.3 (G)
unnamed: R81.1, R85.2, T8.3 (G)
unnamed: R85.1, T7.1 (D)
unnamed: R82.1, R84.2, T7.3 (G)
unnamed: R77.1, T6.2 (S)
unnamed: R83.1, T8.2 (S)
PA6_BATT_OUTPUT_POWER: R68.2; also elsewhere on the board
PC8_MEASURE_ON_UA1: IC6.3 (EN), R67.1, R76.2; also elsewhere on the board
PC9_MEASURE_ON_UA2: IC5.3 (EN), R66.1, R82.2; also elsewhere on the board
PD0_ADC_IA1_IN: IC6.4 (OUT), R72.1; also elsewhere on the board
PD3_ADC_IA2_IN: IC5.4 (OUT), R73.1; also elsewhere on the board
PD6_ADC_UA1_IN: C61.1, R80.2, T6.1 (D); also elsewhere on the board
PD7_ADC_UA2_IN: C62.1, R86.2, T8.1 (D); also elsewhere on the board
UA1: R74.2, R77.2; also elsewhere on the board
UA2: R81.2, R83.2; also elsewhere on the board

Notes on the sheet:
Measure Current mit 12V Pegel
Output Measurements Current&Voltage
Output Measurements Current
Output Measurements Voltage
gemessen: AUS 16uA
BATT_OUTPUT >10V
BATT_OUTPUT AN/AUS schalten!
Taktung der Messungen durch PC8_MEASURE_ON_UA1 PC9_MEASURE_ON_UA2
Teilerverhältnis: 12V:4= 3V (PD6_ADC_UA1_IN;PD7_ADC_UA2_IN)

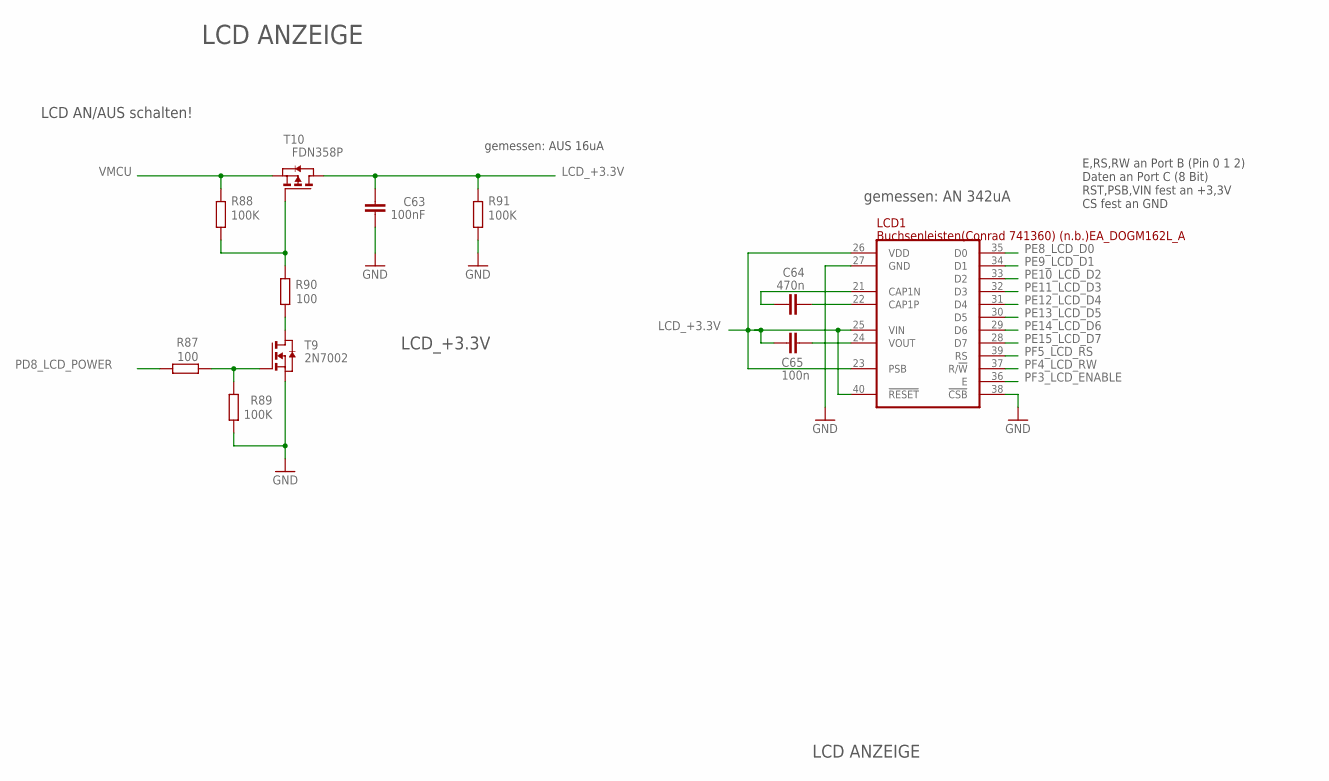
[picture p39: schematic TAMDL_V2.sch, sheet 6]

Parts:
C63: 100nF; C0603
C64: 470n; C0805
C65: 100n; C1206
LCD1: Buchsenleisten(Conrad 741360) (n.b.)EA_DOGM162L_A; EA_DOGM
R87, R90: 100; R0805
R88, R89, R91: 100K; R0805
T9: 2N7002; ZETEX_SOT-23
T10: FDN358P; ZETEX_SOT-23

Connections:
GND: C63.2, LCD1.27 (GND), LCD1.38 (!CSB!), R89.1, R91.1, T9.2 (S); also elsewhere on the board
LCD_+3.3V: C63.1, C65.2, LCD1.23 (PSB), LCD1.25 (VIN), LCD1.26 (VDD), LCD1.40 (!RESET!), R91.2, T10.1 (D)
unnamed: R88.1, R90.2, T10.3 (G)
unnamed: R90.1, T9.1 (D)
unnamed: R87.1, R89.2, T9.3 (G)
unnamed: C64.1, LCD1.21 (CAP1N)
unnamed: C64.2, LCD1.22 (CAP1P)
unnamed: C65.1, LCD1.24 (VOUT)
PD8_LCD_POWER: R87.2; also elsewhere on the board
PE8_LCD_D0: LCD1.35 (D0); also elsewhere on the board
PE9_LCD_D1: LCD1.34 (D1); also elsewhere on the board
PE10_LCD_D2: LCD1.33 (D2); also elsewhere on the board
PE11_LCD_D3: LCD1.32 (D3); also elsewhere on the board
PE12_LCD_D4: LCD1.31 (D4); also elsewhere on the board
PE13_LCD_D5: LCD1.30 (D5); also elsewhere on the board
PE14_LCD_D6: LCD1.29 (D6); also elsewhere on the board
PE15_LCD_D7: LCD1.28 (D7); also elsewhere on the board
PF3_LCD_ENABLE: LCD1.36 (E); also elsewhere on the board
PF4_LCD_RW: LCD1.37 (R/!W!); also elsewhere on the board
PF5_LCD_RS: LCD1.39 (RS); also elsewhere on the board
VMCU: R88.2, T10.2 (S); also elsewhere on the board

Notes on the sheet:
LCD ANZEIGE
E,RS,RW an Port B (Pin 0 1 2) Daten an Port C (8 Bit) RST,PSB,VIN fest an +3,3V CS fest an GND
gemessen: AUS 16uA
LCD_+3.3V
LCD AN/AUS schalten!
gemessen: AN 342uA

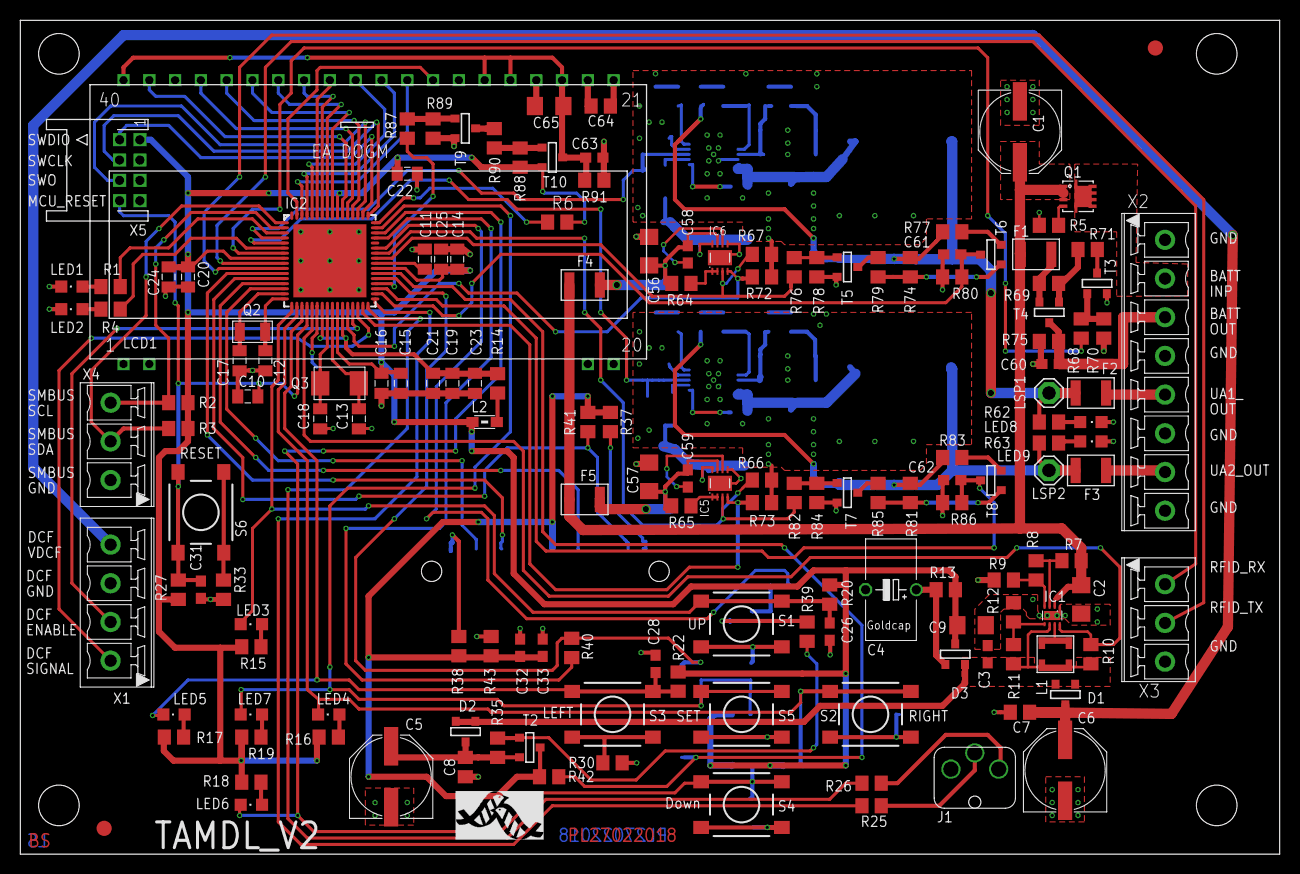
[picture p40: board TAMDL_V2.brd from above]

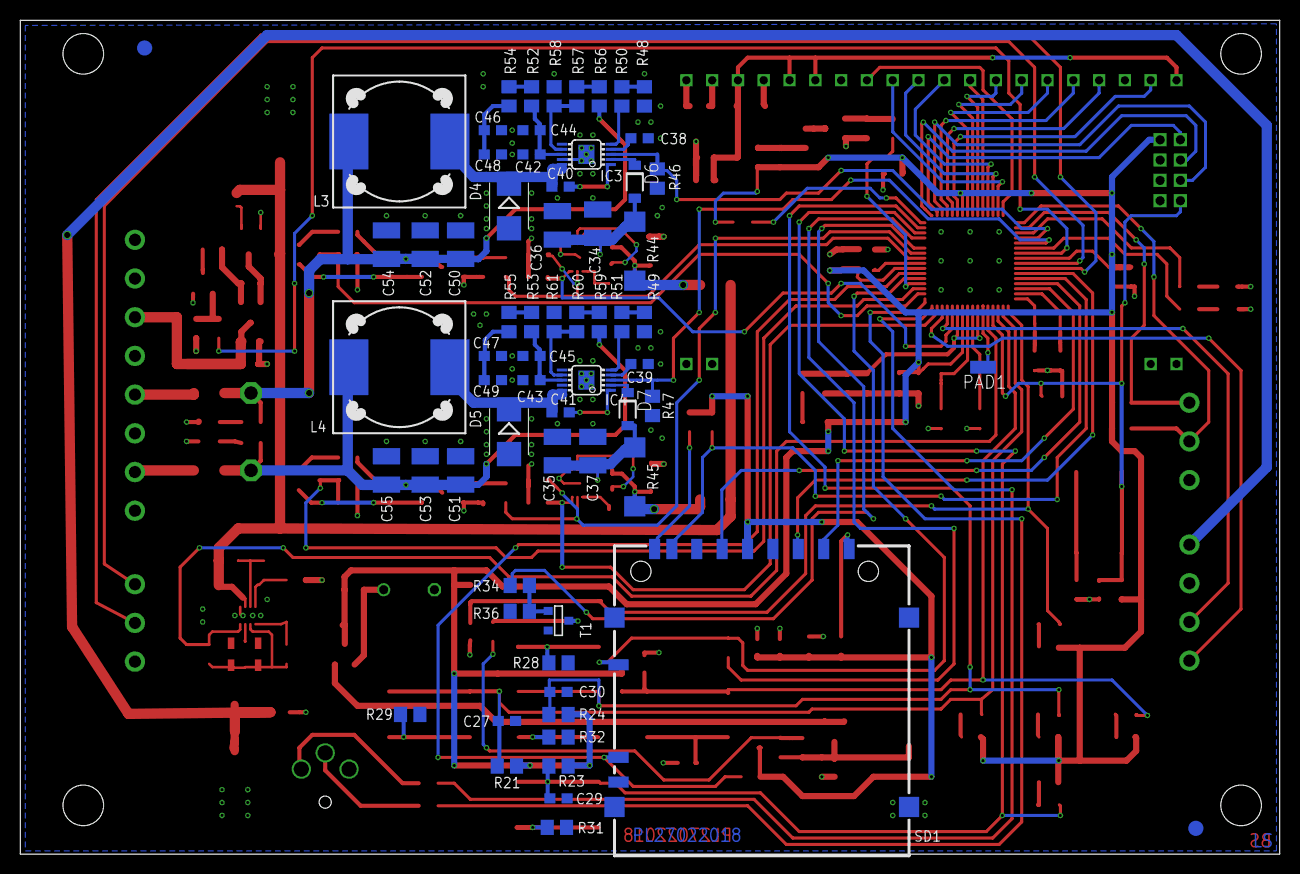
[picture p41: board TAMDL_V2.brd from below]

Board: 2 copper layers, 124.0 x 82.1 mm, 222 parts (65 on the bottom side), 148 nets.

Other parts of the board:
U$1: MPIO-ICON

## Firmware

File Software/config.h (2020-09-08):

/***************************************************************************//**
 * @file
 * @brief	Project configuration file
 * @author	Ralf Gerhauser
 * @version	2020-05-12
 *
 * This file allows to set miscellaneous configuration parameters.  It must be
 * included by all modules.
 *
 ****************************************************************************//*
Revision History:
2020-05-12,rage	Use defines XXX_POWER_ALARM instead of ENUMs.
		Power Alarms are grouped in ON and OFF alarms now.
2016-02-26,rage	Increased LOG_BUF_SIZE to 4KB.
2016-02-10,rage	Set DFLT_RFID_POWER_OFF_TIMEOUT to 6 minutes.
2014-11-11,rage	Derived from project "AlarmClock".
*/

#ifndef __INC_config_h
#define __INC_config_h

/*=============================== Header Files ===============================*/

#include <stdio.h>
#include <stdbool.h>
#include "em_device.h"

/*=============================== Definitions ================================*/

/*
 * Basic defines
 */
    /* terminators for lists and strings */

#define	EOL		NULL		/* EndOfList		*/
#define EOS		'\0'		/* EndOfString		*/
#define	NONE		(-1)

    /* macro to calculate the number of elements of an array */
#define ELEM_CNT(array)  (sizeof (array) / sizeof ((array)[0]))

/*
 * LED Definitions for this project
 */
    /*!@brief GPIO Port of the (red) Power-LED. */
#define POWER_LED_PORT		gpioPortA
    /*!@brief GPIO Pin of the (red) Power-LED is PA2. */
#define POWER_LED_PIN		2
    /*! @brief Macro to set or clear the Power-LED */
#define POWER_LED   IO_Bit(GPIO->P[POWER_LED_PORT].DOUT, POWER_LED_PIN)
    /*!@brief GPIO Port of the (green) Log Flush LED. */
#define LOG_FLUSH_LED_PORT	gpioPortA
    /*!@brief GPIO Pin of the (green) Log Flush LED is PA5. */
#define LOG_FLUSH_LED_PIN	5		//! State: 0=OFF, 1=ON
    /*! @brief Macro to set or clear the Log Flush LED */
#define LOG_FLUSH_LED IO_Bit(GPIO->P[LOG_FLUSH_LED_PORT].DOUT, LOG_FLUSH_LED_PIN)

/*!
 * @brief MPU Clock Configuration.
 *
 * Set to 0 to use the internal RC oscillator, if 1 the external 32MHz XTAL
 * is used.  The frequency of the RC oscillator is 14MHz per default.
 */
#define USE_EXT_32MHZ_CLOCK	1

/*
 * Configuration for module "AlarmClock"
 */
    /*!@brief RTC frequency in [Hz]. */
#define RTC_COUNTS_PER_SEC	32768


/*!
 * @brief Interrupt Priority Settings
 *
 * There are 8 priority levels 0 to 7 with 0 to be the highest and 7 to be
 * the lowest priority.  ADC measurement requires high priority, otherwise
 * data gets lost.  DCF77 (which is called from the EXTI handler) and RTC
 * must use the same priority level to lock-out each other, because they
 * both use function localtime() and this is not multithreading save.
 * Funktion localtime_r() would be the right choice here, unfortunately it
 * is not available with the IAR compiler library.
 */
#define INT_PRIO_ADC	0		//!< ADC has highest priority
#define INT_PRIO_UART	2		//!<  UART interrupts for the RFID reader
#define INT_PRIO_LEUART	2		//!<  LEUART RX interrupt (not used)
#define INT_PRIO_DMA	2		//!<  DMA is used for LEUART
#define INT_PRIO_SMB	2		//!<  SMBus used by the battery monitor
#define INT_PRIO_RTC	3		//!<  lower priority than others
#define INT_PRIO_EXTI	INT_PRIO_RTC	//!<  must be the same as @ref INT_PRIO_RTC

/*
 * Configuration for module Keys
 */
    /*! Enable autorepeat functionality. */
#define KEY_AUTOREPEAT	1
    /*! Time in [ms] a key needs to be asserted to start autorepeat. */
#define AUTOREPEAT_THRESHOLD	750
    /*! Rate in [ms] the autorepeat feature repeats the previous key. */
#define AUTOREPEAT_RATE		250


/*
 * Configuration for Atomic Clock module "DCF77.c"
 */
    /*!@brief Use Hardware Enable pin of the DCF77 receiver. */
#define DCF77_HARDWARE_ENABLE	1

    /*!@brief Activate DCF77 only once per day. */
#define DCF77_ONCE_PER_DAY	1

    /*!@brief Call ShowDCF77Indicator() to flash red LED on DCF77 signal. */
#define DCF77_INDICATOR		1


/*
 * Configuration for module "RFID"
 */
    /*!@brief Flag, if RFID reader is triggered by a light barrier. */
#define RFID_TRIGGERED_BY_LIGHT_BARRIER	0	// NO light barrier present


/*
 * Configuration for module "Logging"
 */
    /*!@brief Size of the log buffer in bytes. */
#define LOG_BUF_SIZE	4096

    /*!@brief Use this define to specify a function to be called for monitoring
     * the log activity.  Here, monitoring is done via the LEUART interface.
     */
#define LOG_MONITOR_FUNCTION	drvLEUART_puts

/* forward declaration */
void    drvLEUART_puts(const char *str);

    /*!@brief Disable "alive" message by setting this interval to 0. */
#define LOG_ALIVE_INTERVAL	0


/*!@name DMA Channel Assignment
 *
 * The following definitions assign the 8 DMA channels to the respective
 * devices or drivers.  These defines are used as index within the global
 * DMA_DESCRIPTOR_TypeDef structure @ref g_DMA_ControlBlock.
 */
//@{
#define DMA_CHAN_LEUART_RX	0	//!< LEUART Rx uses DMA channel 0
#define DMA_CHAN_LEUART_TX	1	//!< LEUART Tx uses DMA channel 1
//@}


/*================================== Macros ==================================*/

#ifdef DEBUG
    /*
     * Debugging output via ITM or LEUART
     */
    #if DEBUG_VIA_ITM
	#define DBG_PUTC(ch)	ITM_SendChar(ch)
	#define DBG_PUTS(str)	ITM_SendStr(str)
	uint32_t ITM_SendChar (uint32_t ch);
	void ITM_SendStr(const char *pStr);
    #else
	#define DBG_PUTC(ch)	drvLEUART_putc(ch)
	#define DBG_PUTS(str)	drvLEUART_puts(str)
	void	drvLEUART_putc(char ch);
	void	drvLEUART_puts(const char *str);
    #endif
    void dbgInit(void);
#else
    #define DBG_PUTC(ch)
    #define DBG_PUTS(str)
#endif

#define INCLUDE_DEBUG_TRACE 0
#if INCLUDE_DEBUG_TRACE
    #define DEBUG_TRACE(id)	DebugTrace(id)
    #define DEBUG_TRACE_STOP	DebugTraceStop()
    void DebugTrace(uint32_t id);
    void DebugTraceStop(void);
    #undef  LOG_BUF_SIZE
    #define LOG_BUF_SIZE	2048
    #define DEBUG_TRACE_COUNT	512
#else
    #define DEBUG_TRACE(id)
    #define DEBUG_TRACE_STOP
#endif

    /*! Macro to address a single bit in the I/O range (peripheral range) in
     *  an atomic manner.
     * @param address   I/O register address.
     * @param bitNum    Bit number within this register.
     */
#define IO_BIT_ADDR(address, bitNum)					\
	((__IO uint32_t *) (BITBAND_PER_BASE				\
			+ (((uint32_t)(address)) - PER_MEM_BASE) * 32	\
			+ (bitNum) * 4))

    /*! Shortcut to directly access an I/O-bit. */
#define IO_Bit(regName, bitNum)	*IO_BIT_ADDR(&regName, bitNum)

    /*! Macro to address a single bit in an SRAM variable in an atomic manner.
     * @param address   Address of the variable in SRAM.
     * @param bitNum    Bit number within this variable.
     */
#define SRAM_BIT_ADDR(address, bitNum)					\
	((__IO uint32_t *) (BITBAND_RAM_BASE				\
			+ (((uint32_t)(address)) - RAM_MEM_BASE) * 32	\
			+ (bitNum) * 4))

    /*! Shortcut to directly access a bit in a variable. */
#define Bit(varName, bitNum)	*SRAM_BIT_ADDR(&varName, bitNum)

/*=========================== Typedefs and Structs ===========================*/

/*!@brief Structure to hold Project Information */
typedef struct
{
    char const  ID[12];
    char const  Date[16];
    char const  Time[10];
    char const  Version[16];
} PRJ_INFO;


/*!@brief Enumeration of Alarm Identifiers
 *
 * This is the list of Alarm IDs used by this application.  They are used to
 * identify a particular alarm time entry via the <b>alarmNum</b> parameter
 * when calling alarm functions, e.g. AlarmSet().
 * The configurable Power Alarms must be grouped in ON and OFF alarms to be able
 * to use a single index for all, see CheckAlarmTimes() and AlarmPowerControl().
 */
typedef enum
{
    ALARM_DCF77_WAKE_UP,    //!< Wake up DCF77 to synchronize the system clock
    ALARM_BATTERY_MON_1,    //!< Time #1 for logging battery status
    ALARM_BATTERY_MON_2,    //!< Time #2 for logging battery status
 // List of programmable Alarm ON Times
    ALARM_UA1_ON_TIME_1,    //!< Time #1 when to switch UA1 output ON
    ALARM_UA1_ON_TIME_2,    //!< Time #2 when to switch UA1 output ON
    ALARM_UA1_ON_TIME_3,    //!< Time #3 when to switch UA1 output ON
    ALARM_UA1_ON_TIME_4,    //!< Time #4 when to switch UA1 output ON
    ALARM_UA1_ON_TIME_5,    //!< Time #5 when to switch UA1 output ON
    ALARM_UA2_ON_TIME_1,    //!< Time #1 when to switch UA2 output ON
    ALARM_UA2_ON_TIME_2,    //!< Time #2 when to switch UA2 output ON
    ALARM_UA2_ON_TIME_3,    //!< Time #3 when to switch UA2 output ON
    ALARM_UA2_ON_TIME_4,    //!< Time #4 when to switch UA2 output ON
    ALARM_UA2_ON_TIME_5,    //!< Time #5 when to switch UA2 output ON
    ALARM_BATT_ON_TIME_1,   //!< Time #1 when to switch BATT output ON
    ALARM_BATT_ON_TIME_2,   //!< Time #2 when to switch BATT output ON
    ALARM_BATT_ON_TIME_3,   //!< Time #3 when to switch BATT output ON
    ALARM_BATT_ON_TIME_4,   //!< Time #4 when to switch BATT output ON
    ALARM_BATT_ON_TIME_5,   //!< Time #5 when to switch BATT output ON
 // List of programmable Alarm OFF Times
    ALARM_UA1_OFF_TIME_1,   //!< Time #1 when to switch UA1 output OFF
    ALARM_UA1_OFF_TIME_2,   //!< Time #2 when to switch UA1 output OFF
    ALARM_UA1_OFF_TIME_3,   //!< Time #3 when to switch UA1 output OFF
    ALARM_UA1_OFF_TIME_4,   //!< Time #4 when to switch UA1 output OFF
    ALARM_UA1_OFF_TIME_5,   //!< Time #5 when to switch UA1 output OFF
    ALARM_UA2_OFF_TIME_1,   //!< Time #1 when to switch UA2 output OFF
    ALARM_UA2_OFF_TIME_2,   //!< Time #2 when to switch UA2 output OFF
    ALARM_UA2_OFF_TIME_3,   //!< Time #3 when to switch UA2 output OFF
    ALARM_UA2_OFF_TIME_4,   //!< Time #4 when to switch UA2 output OFF
    ALARM_UA2_OFF_TIME_5,   //!< Time #5 when to switch UA2 output OFF
    ALARM_BATT_OFF_TIME_1,  //!< Time #1 when to switch BATT output OFF
    ALARM_BATT_OFF_TIME_2,  //!< Time #2 when to switch BATT output OFF
    ALARM_BATT_OFF_TIME_3,  //!< Time #3 when to switch BATT output OFF
    ALARM_BATT_OFF_TIME_4,  //!< Time #4 when to switch BATT output OFF
    ALARM_BATT_OFF_TIME_5,  //!< Time #5 when to switch BATT output OFF
    NUM_ALARM_IDS
} ALARM_ID;

/*
 * !@brief These defines hold the first and last alarm time ENUM for Power
 * Output control, and the number of alarm ON, resp. OFF times.
 */
//@{
#define FIRST_POWER_ALARM	ALARM_UA1_ON_TIME_1
#define LAST_POWER_ALARM	ALARM_BATT_OFF_TIME_5
#define NUM_POWER_ALARMS	(LAST_POWER_ALARM - ALARM_UA1_OFF_TIME_1 + 1)
//@}

/*
 * !@brief The following defines set the first on and off alarm, and the number
 * of alarm time entries of a specific power output.
 */
//@{
#define FIRST_ALARM_ON_TIME	ALARM_UA1_ON_TIME_1
#define FIRST_ALARM_OFF_TIME	ALARM_UA1_OFF_TIME_1
#define NUM_ALARM_UA1		5
#define NUM_ALARM_UA2		5
#define NUM_ALARM_BATT		5
//@}


/*!@brief Enumeration of the EM1 Modules
 *
 * This is the list of Software Modules that require EM1 to work, i.e. they
 * will not work in EM2 because clocks, etc. would be disabled.  These enums
 * are used to set/clear the appropriate bit in the @ref g_EM1_ModuleMask.
 */
typedef enum
{
    EM1_MOD_RFID,	//!<  0: The RFID Module uses the UART
    EM1_MOD_ADC,	//!<  1: ADC is a HFPER clock device
    END_EM1_MODULES
} EM1_MODULES;

/*======================== External Data and Routines ========================*/

extern volatile bool	 g_flgIRQ;		// Flag: Interrupt occurred
extern volatile uint16_t g_EM1_ModuleMask;	// Modules that require EM1


#endif /* __INC_config_h */

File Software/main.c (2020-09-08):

/***************************************************************************//**
 * @file
 * @brief	TAMDL
 * @author	Ralf Gerhauser
 * @version	2020-05-12
 *
 * This application consists of the following modules:
 * - main.c - Initialization code and main execution loop.
 * - DMA_ControlBlock.c - Control structures for the DMA channels.
 * - Control.c - Sequence Control module.
 * - CfgData.c - Handling of configuration data.
 * - ExtInt.c - External interrupt handler.
 * - Keys.c - Key interrupt handling and translation.
 * - AlarmClock.c - Alarm clock and timers facility.
 * - DCF77.c - DCF77 Atomic Clock Decoder
 * - clock.c - An implementation of the POSIX time() function.
 * - LCD_DOGM162.c - Driver for the DOGM162 LC-Display.
 * - DisplayMenu.c - Display manager for Menus and LCD.
 * - DM_Clock_Transp.c - Display Module to show Clock and Transponder number
 * - DM_PowerOutput.c - Display Module to switch @ref Power_Outputs
 * - DM_BatteryStatus.c - Display Module to show current Battery Status
 * - DM_PowerTimes.c - Display Module to show all configured ON/OFF Times.
 * - RFID.c - RFID reader to receive transponder IDs.
 * - BatteryMon.c - Battery monitor, periodically reads the state of the
 *   battery via the SMBus.
 * - LEUART.c - The Low-Energy UART can be used as monitoring and debugging
 *   connection to a host computer.
 * - microsd.c - Together with the files "diskio.c" and "ff.c", this module
 *   provides an implementation of a FAT file system on the @ref SD_Card.
 * - Logging.c - Logging facility to send messages to the LEUART and store
 *   them into a file on the SD-Card.
 * - eeprom_emulation.c - Routines to store data in Flash, taken from AN0019.
 * - PowerFail.c - Handler to switch off all loads in case of Power Fail.
 *
 * Parts of the code are based on the example code of AN0006 "tickless calender"
 * and AN0019 "eeprom_emulation" from Energy Micro AS.
 *
 ***************************************************************************//**
 *
 * Parts are Copyright 2013 Energy Micro AS, http://www.energymicro.com
 *
 *******************************************************************************
 *
 * Permission is granted to anyone to use this software for any purpose,
 * including commercial applications, and to alter it and redistribute it
 * freely, subject to the following restrictions:
 *
 * 1. The origin of this software must not be misrepresented; you must not
 *    claim that you wrote the original software.
 * 2. Altered source versions must be plainly marked as such, and must not be
 *    misrepresented as being the original software.
 * 3. This notice may not be removed or altered from any source distribution.
 * 4. The source and compiled code may only be used on Energy Micro "EFM32"
 *    microcontrollers and "EFR4" radios.
 *
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
 * Energy Micro AS will not be liable for any consequential, incidental, or
 * special damages, or any other relief, or for any claim by any third party,
 * arising from your use of this Software.
 *
 ****************************************************************************//*
Revision History:
2020-05-12,rage	Call CheckAlarmTimes() after CONFIG.TXT has been read.
2018-10-09,rage	Moved DMA related variables to module "DMA_ControlBlock.c".
		Calling VerifyConfiguration() ensures data is valid.
2018-03-02,rage	Initial version.
*/
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

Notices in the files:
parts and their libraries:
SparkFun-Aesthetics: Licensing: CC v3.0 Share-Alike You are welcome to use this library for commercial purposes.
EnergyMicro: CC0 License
